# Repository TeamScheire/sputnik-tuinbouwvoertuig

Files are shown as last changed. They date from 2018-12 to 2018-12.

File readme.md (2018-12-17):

# Sputnik - de tuinbouwmachine

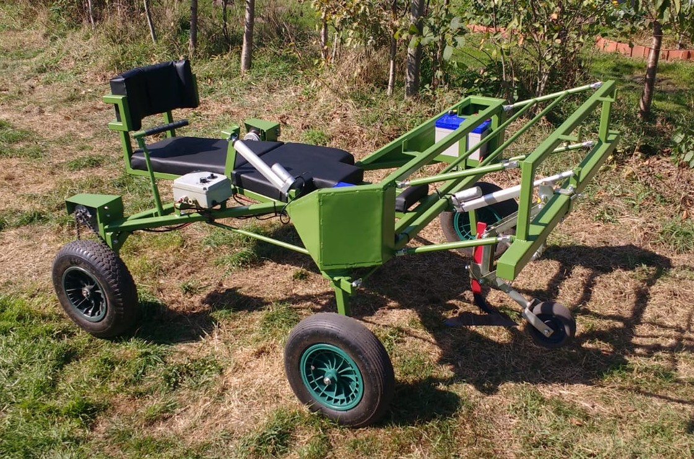
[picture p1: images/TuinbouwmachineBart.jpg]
sputnik


De sputnik is een tuinbouwmachine, speciaal en op maat gemaakt voor Bart, een persoon die een biologische deeltuin heeft, maar door een ski-ongeval in een rolstoel zit.

[Ronald Van Ham](https://github.com/RonaldVanHam) en [Elisa Van Coster](http://www.studiobasalt.be) werkten samen. Elisa ontwierp de machine en maakte het frame en besturing. Ronald deed de aansturing van de motoren.

In deze repo vind je:

- [Afbeeldingen](./images) met de afmetingen en details van de constructie
- [Broncode](./software) van de software
- [Ontwerpen](./designs) van de tandwielen en andere mechanicaonderdelen

## Frame

### Ontwerp

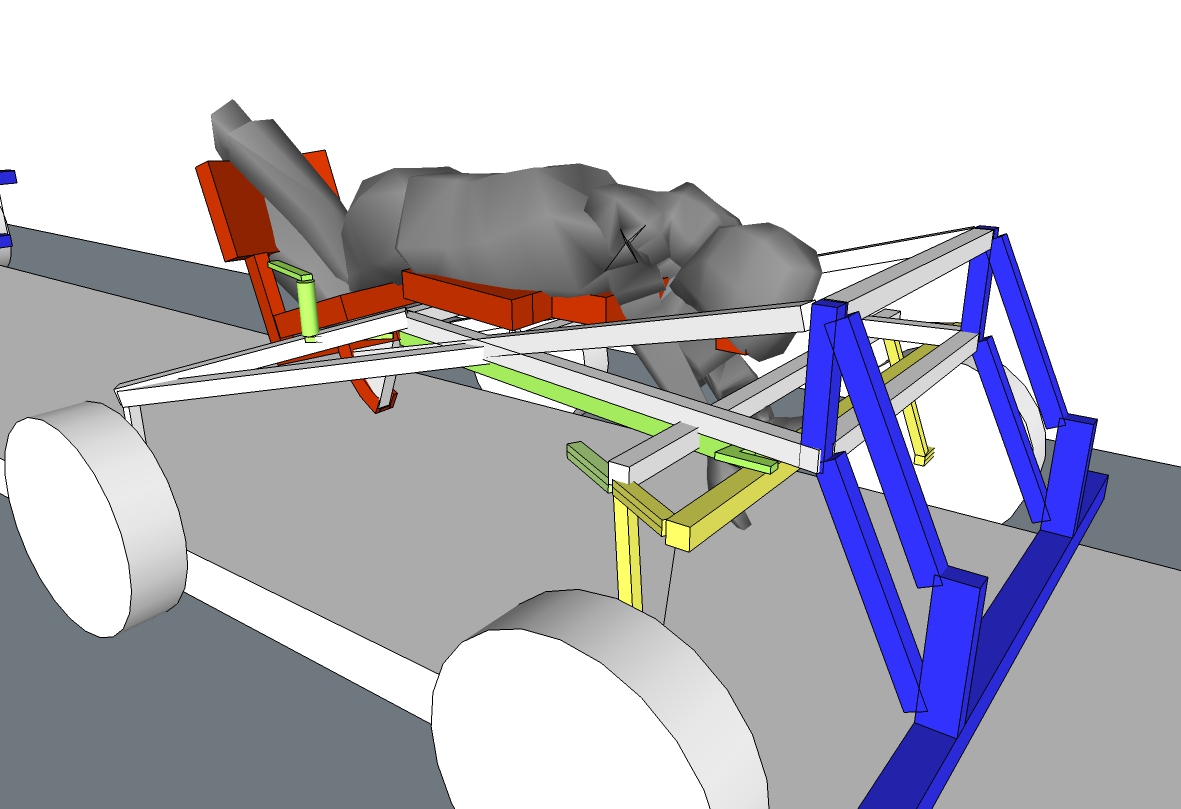
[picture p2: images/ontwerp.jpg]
ontwerp


- De gele delen zijn de onderdelen van het stuur.
- De rode delen zijn die van de stoel die in zit- en lighouding gezet kan worden.
- De blauwe delen zijn die van de werktuigenbalk die in hoogte versteld kan worden.

### Afmetingen

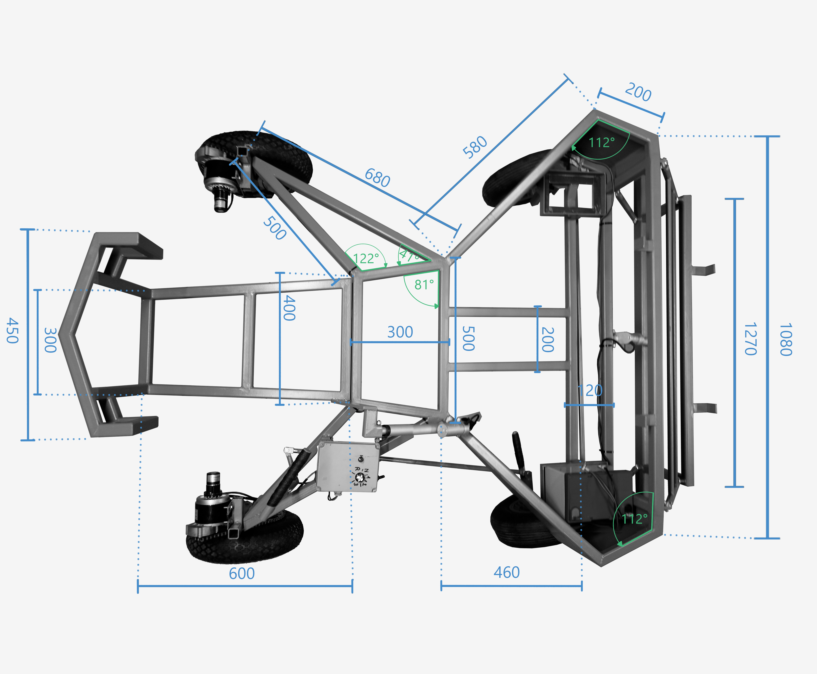
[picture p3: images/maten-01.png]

afmetingen-02

### Stuur

Het stuur zit op de voorstel wielen en is gebouwd volgens het [Ackermannprincipe](https://nl.wikipedia.org/wiki/Ackermann-principe)

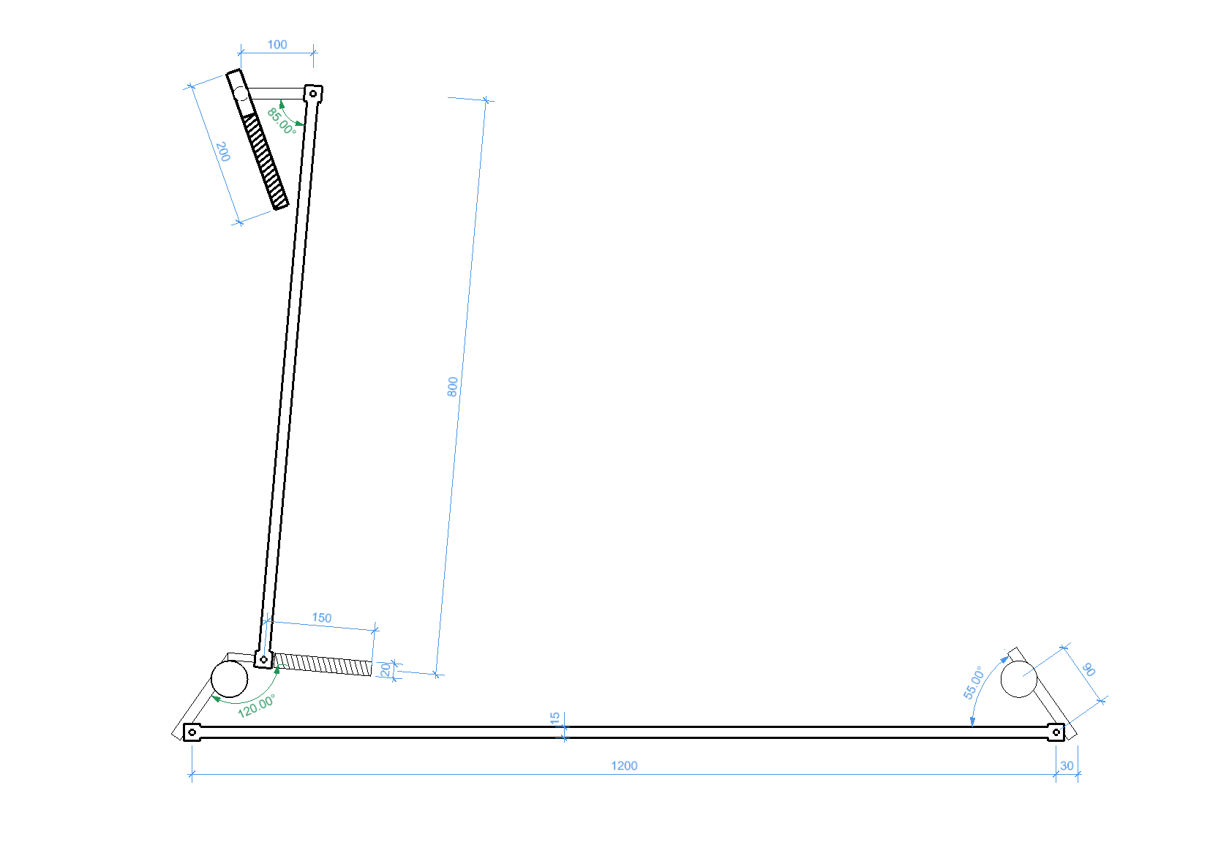
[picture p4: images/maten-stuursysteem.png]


### Details

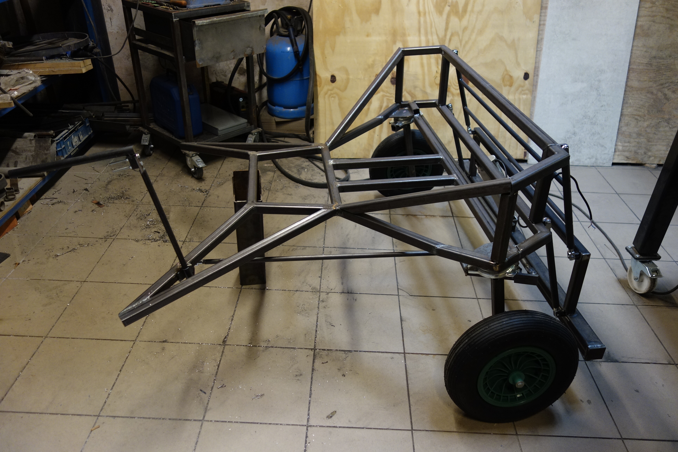
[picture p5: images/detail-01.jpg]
detail-01

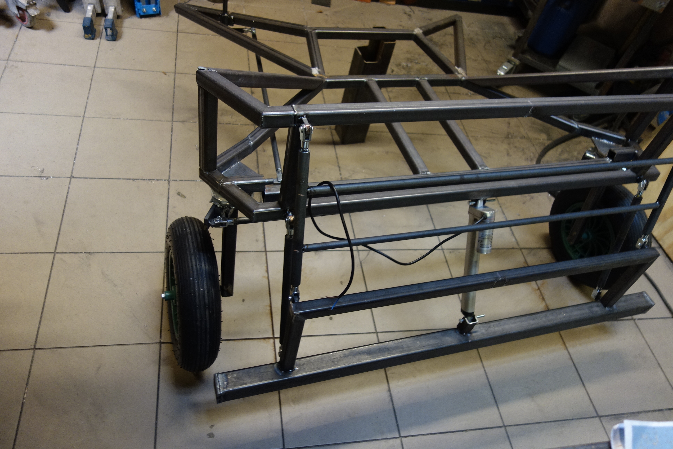
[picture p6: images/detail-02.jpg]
detail-02

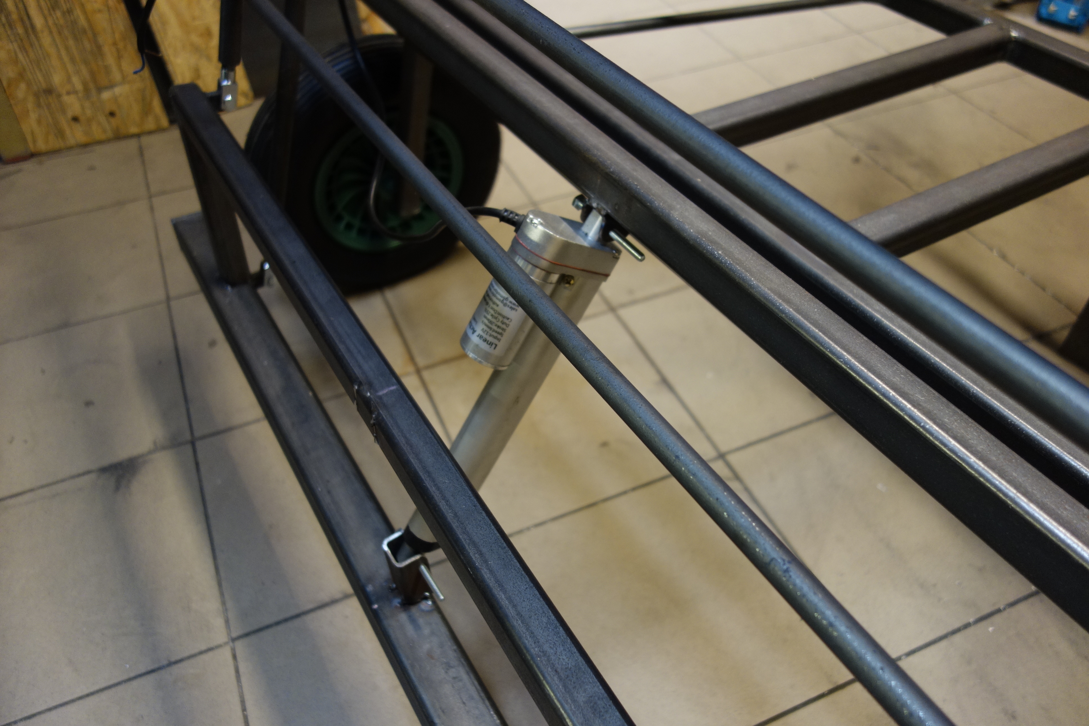
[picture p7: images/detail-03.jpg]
detail-03

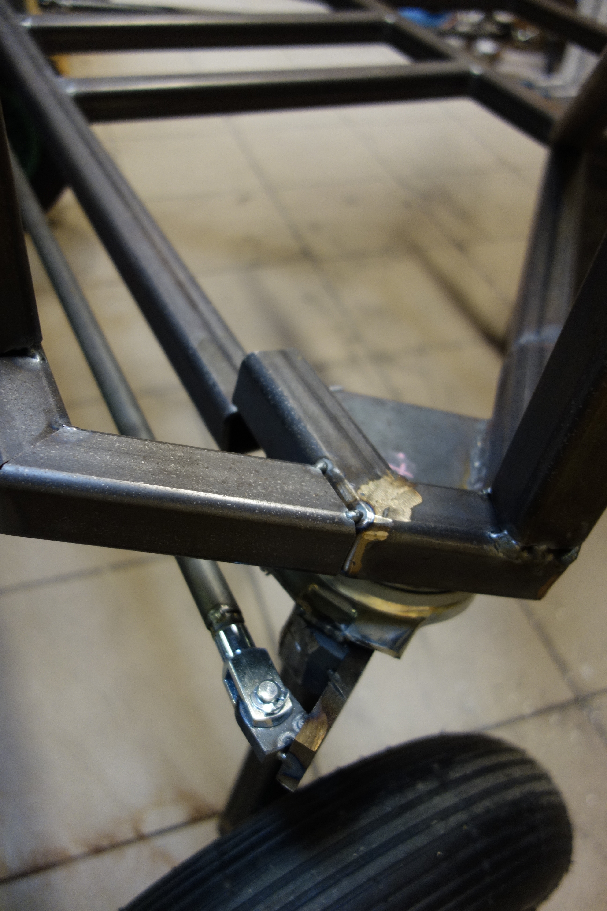
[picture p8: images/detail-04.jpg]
detail-04

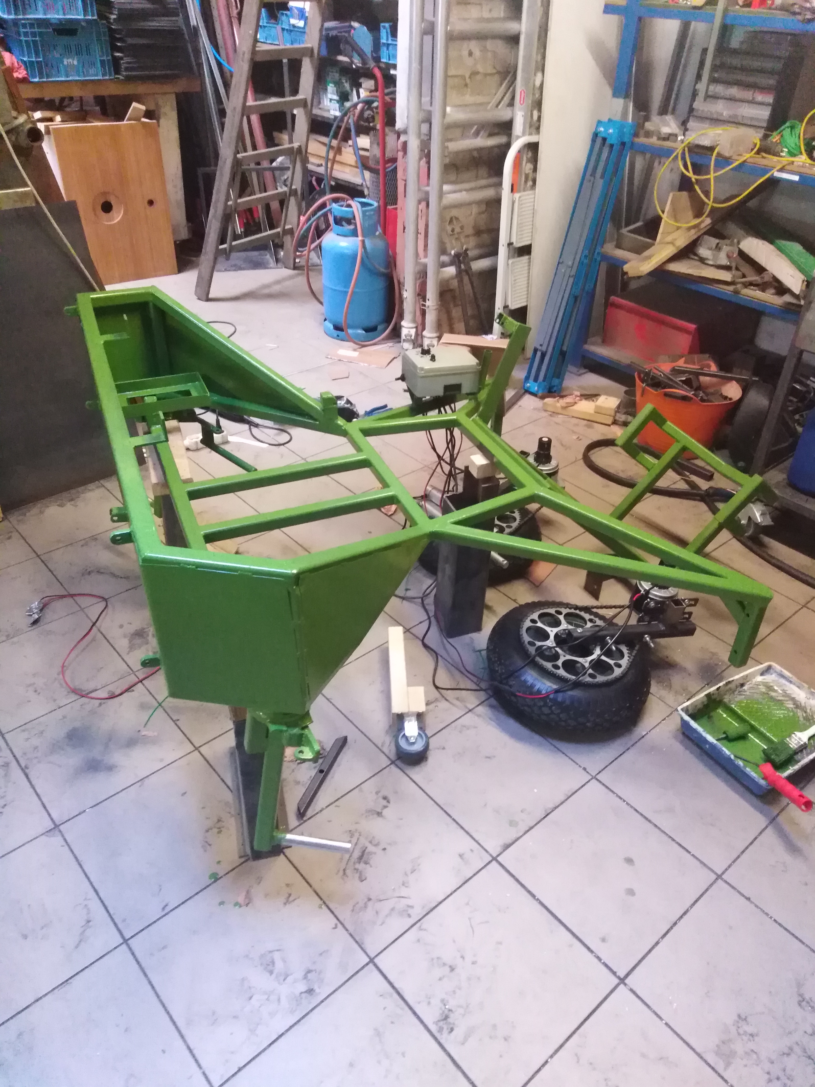
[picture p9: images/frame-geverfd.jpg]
geverfd
 	

## Motoren

Om over de gewassen te kunnen rijden met aandrijving zijn er in principe 2 opties: 

Eén motor gebruiken en de twee wielen verbinden met een as *of* twee keer op elk wiel een motor zetten. 

Bart wil kunnen zitten en liggen. Het zaaibed is bovendien hoger dan de zijpaden waar de wielen op rusten. Een as zou dus de gewassen raken. Vandaar is het snel duidelijk dat een motor op elk wiel de enige optie is.

### Aandrijving

De motoren die gebruikt worden voor de aandrijving, zijn te verkrijgen via [ali express](https://www.aliexpress.com/w/my1016z-12v.html) of [forandor](https://forandor.com/index.php?route=product/product&path=68&product_id=324)

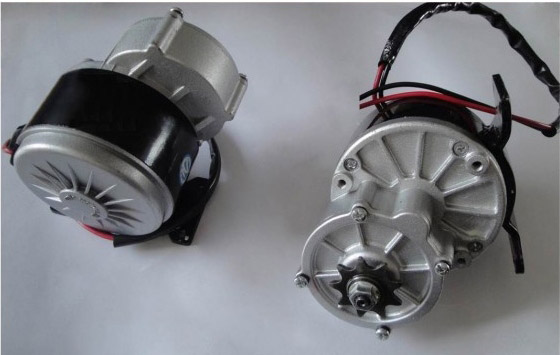
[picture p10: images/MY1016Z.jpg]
motor


### Lineaire actuatoren

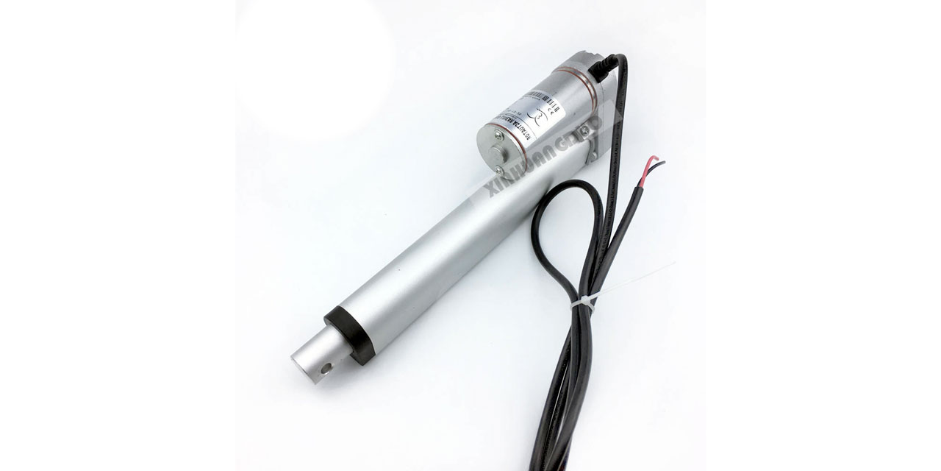
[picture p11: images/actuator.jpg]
Lineaire Actuatoren


De motoren die gebruikt zijn voor de beweging van de stoel en de werktuigenbalk zijn lineaire actuatoren. Deze zijn [hier te krijgen](https://www.aliexpress.com/item/Free-shipping-24v-150mm-6inch-stroke-mini-linear-actuator-electric-linear-actuator-thrust-900N-customized-stroke/1647892597.html) en hebben een stang die op en neer kan bewegen in een nauwkeurige positie.

## Aandrijving

De extra uitdaging is dat Bart zowel snel, maar vooral heel traag wil kunnen rijden. Normaal wordt hiervoor een motor met een mechanische versnellingsbak gebruikt, zoals bijvoorbeeld ook in een auto zit.

Maar er zijn twee motoren en twee versnellingsbakken zou het geheel vrij zwaar en de bediening moeilijk maken. Ze moeten immers altijd in dezelfde versnelling staan.

Een DC motor gebruiken heeft het nadeel dat als je de DC heel traag wil later draaien, je de spanning zo laag moet maken dat ook de stroom en het koppel te klein wordt om nuttig te zijn. Dus de motor gaat waarschijnlijk gewoon niet draaien. 

### Closed loop

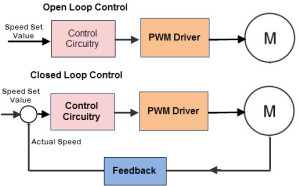
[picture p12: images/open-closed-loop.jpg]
closed loop


De DC motor wordt op een speciale manier aangestuurt, namelijk in 'closed loop'. Dat wil zeggen dat een snelheidsregelaar gebruikt wordt, geprogrammeerd in de [Arduino](./software/TuinbouwmachineBart/TuinbouwmachineBart.ino). 

We krijgen aan de ene kant een gevraagde snelheid via de potentiometer die Bart kan regelen. We gaan die in de controller vergelijken met de huidige snelheid die we meten via de optische encoder op de motor. We maken in de controller het verschil van deze twee snelheden. Dit noemen we de ‘fout’ (error) tussen wat we vragen en wat we meten. Deze fout gaan we gebruiken om de waarde van de PWM te bepalen. We gaan de fout met een bepaalde waarde vermenigvuldigen om de PWM waarde te krijgen, deze waarde noemen we de proportionele constante van onze regelaar. 

Dit gaat al redelijk werken, maar we merken op heel lage snelheden dat de motor toch gaat stilstaan, omdat de fout dan ook klein gaat zijn en de PWM waarde ook klein. Om dit op te lossen gaan we de fout 'integreren'. Dit wil zeggen dat we telkens de fout optellen en deze waarde vermenigvuldigen met een andere constante, de integrale constante van onze regelaar. Op deze manier gaat de PWM waarde verhogen als we langere tijd te traag draaien (of blijven stil staan). 

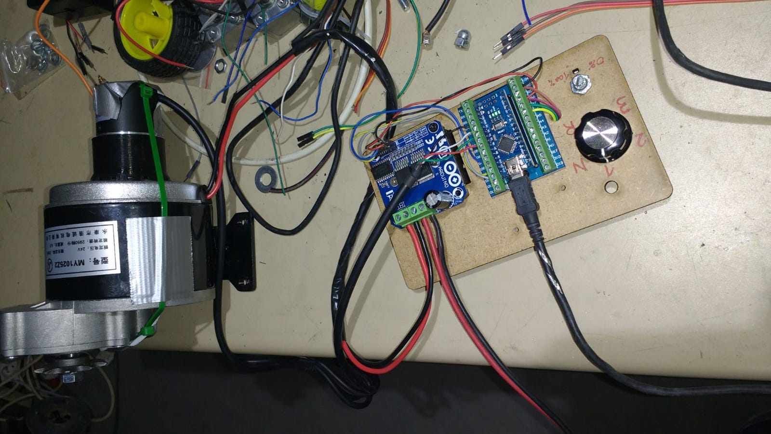
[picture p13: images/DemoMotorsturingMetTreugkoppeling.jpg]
demoopstelling


Nu komt het er op aan de 2 constanten van onze PI regelaar (proportioneel en integraal regelaar) juist in te stellen. Dit kan theoretisch aangepakt worden of we kunnen ze tunen ‘in the field’. Dit laatste is letterlijk te nemen, want Bart wil dat zijn machine traag door een veld kan rijden. Dit wil zeggen dat de weerstand kan veranderen naargelang er meer grond voor de wielen ligt of hij aan het rijden of schoffelen is. Dit theoretisch benaderen is moeilijk, want we hebben geen waarden van de weerstand die Bart gaat ondervinden op zijn veld. 

In dit geval hebben we bij deze waarden wel wat marge omdat gaat het om een tuinbouwmachine, waarbij de snelheid moet geregeld kunnen worden, maar ook niet super precies hoeft te zijn. Dus we gaan de waarden in ons atelier instellen en nadien aanpassen op het veld indien nodig.

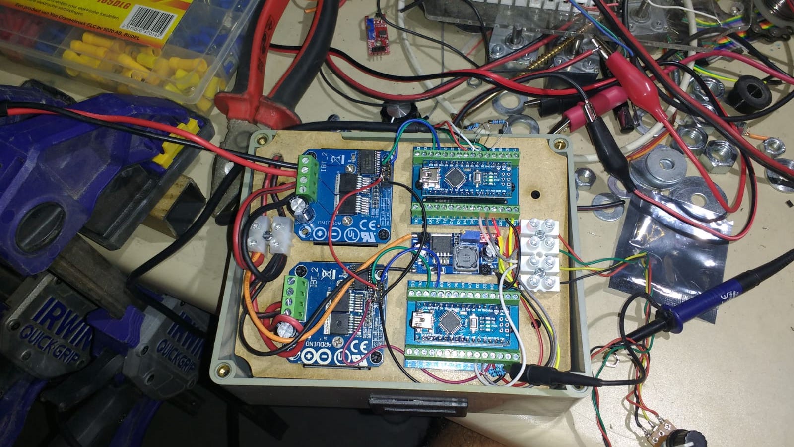
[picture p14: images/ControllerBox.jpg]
controllerbox


### De instelling van de gevraagde snelheid.

Omdat een potentiometer in de lage snelheden moeilijk in te stellen is, werken we met softwarematige versnellingen. We hebben een 2de knop geplaatst waarmee Bart kan kiezen tussen 1 versnelling achteruit, neutraal en 3 versnellingen vooruit. Dus de software gaat bij de achteruitstand van de knop, de richting van de motor omdraaien en de gevraagde snelheid beperken. Achteruit moet Bart immers niet zo snel kunnen rijden. Vooruit hebben we de snelheid in 3 stappen ingesteld. In 3de versnelling kunnen we de motor op volle snelheid aansturen, in 2de ongeveer zo snel als achteruit, en in 1ste heel traag. Dus de volledige toer van de potentiometer wordt herschaald naar een beperkt deel van de snelheid. Zo kan Bart ook op lage snelheden zijn gevraagde snelheid vrij precies instellen.

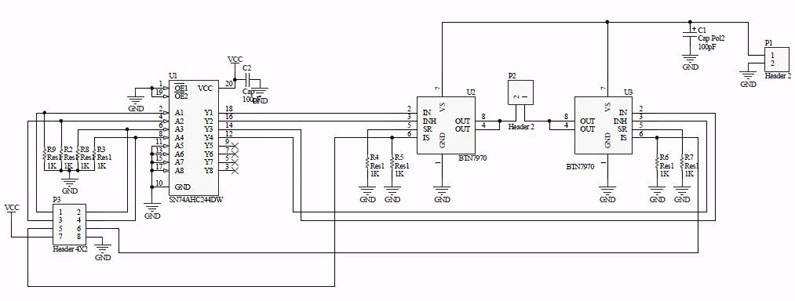
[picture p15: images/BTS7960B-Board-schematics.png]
schematics


We hebben dus 2 snelheidsgestuurde motoren. Gevolg is dat de 2 wielen ook quasi even snel gaan draaien. Dit komt overeen met een starre achteras, dus zonder differentieel. Een differentieel bij een auto is een mechanisme met tandwielen dat toelaat dat de 2 wielen met een verschillende snelheid draaien. Dit is nodig als je een bocht neemt met een auto. Door onze 2 motoren in snelheid te sturen gaan de wielen in een  bocht even snel draaien en dus op de grond slippen. Om dit te vermijden gaan we in 3de versnelling en in achteruit de controle open loop doen, dus geen snelheidsterugkoppeling, en dus een soort softwarematige of elektrische differentieel. In 1ste en 2de gaat de closed loop werken, omdat we dan normaal geen grote bochten gaan maken en we daar die closed loop controle nodig hebben om de motoren traag te kunnen laten draaien. Hier rijden we dan alsof we een ‘sper-differentieel’ of starre achteras hebben.

### Andere types motoren

We hebben geopteerd voor een DC motor omdat dit voor de meeste makers gemakkelijker is in gebruik. Er bestaan ook brushless DC motoren (zonder koolborstels en met elektronische commutatie). Deze kunnen ook open loop en closed loop gebruikt worden. Om de positie en snelheid te meten, gebruiken deze meestal Hall sensoren. Deze dienen om de elektronische commutatie goed te kunnen aansturen maar zorgen ook meteen voor een feedback op de snelheid. Dit is te vergelijken met de encoder en closed loop DC motor die wij gebouwd hebben, alleen is de driver wat complexer in gebruik en ook complexer om uit te leggen tegenover de H-Brug bij de gewone DC motor.

## Afgewerkt

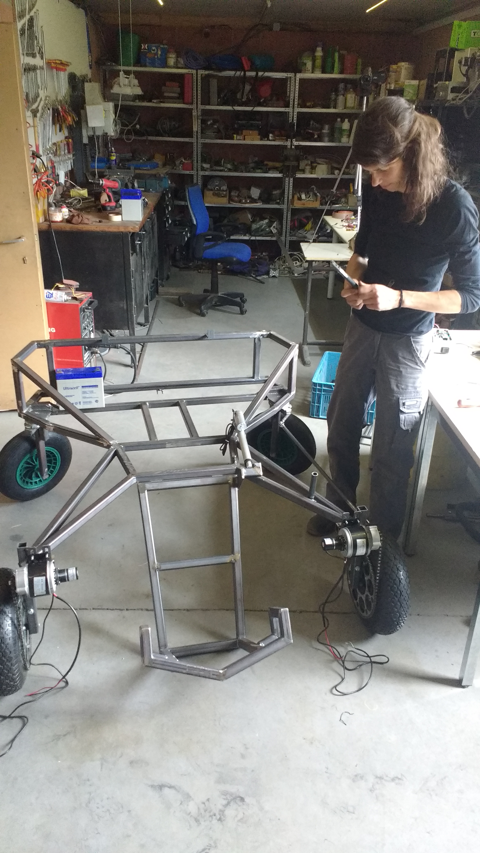
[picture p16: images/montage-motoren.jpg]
motoren

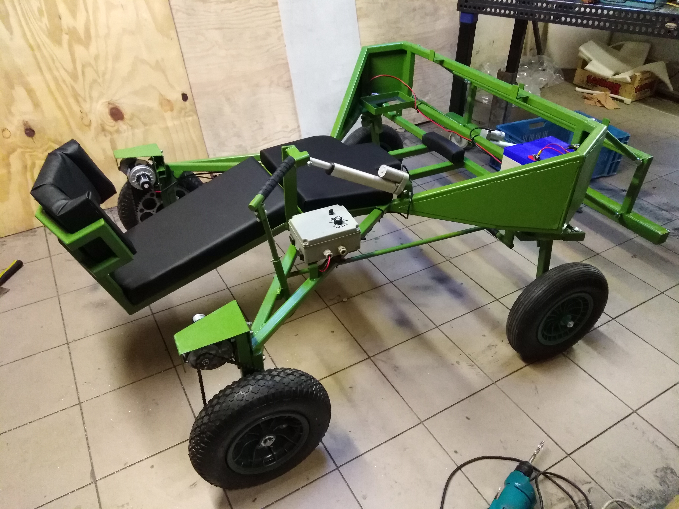
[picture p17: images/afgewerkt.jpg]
afgewerkt


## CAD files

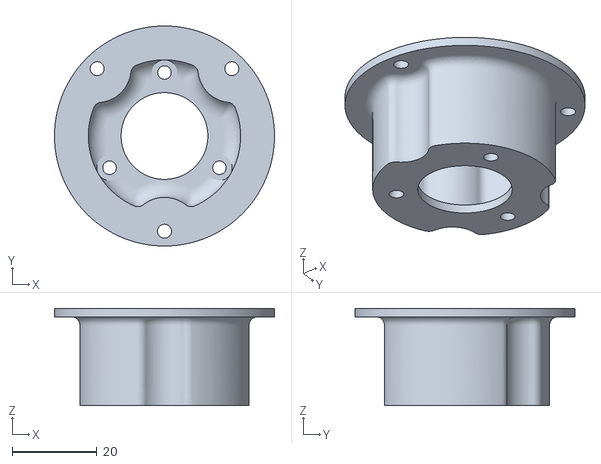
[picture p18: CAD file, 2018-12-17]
designs/EncoderHouder Potje om te schroeven.stl
52.0 x 52.0 x 23.0

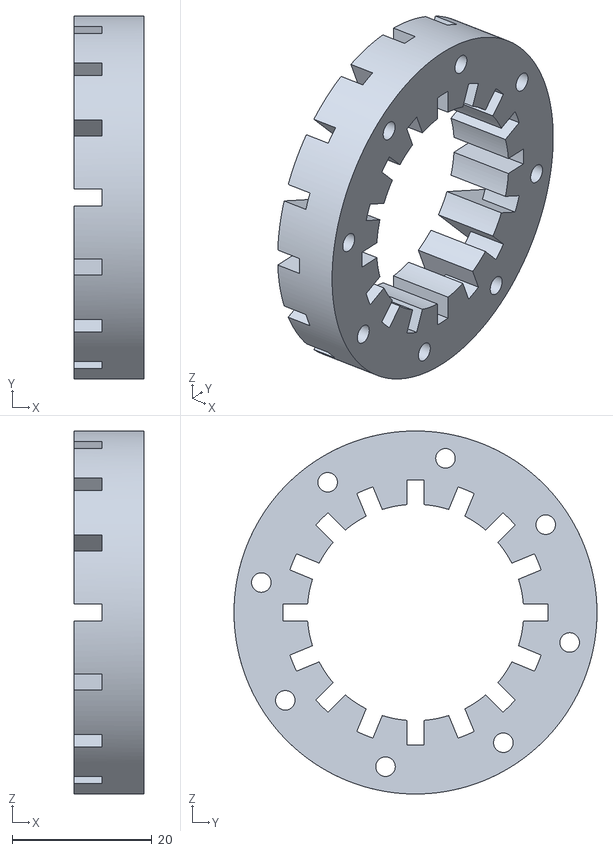
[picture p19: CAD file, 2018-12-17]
designs/EncoderHouder Lijmstuk op MY1016.stl
10.0 x 52.0 x 52.0

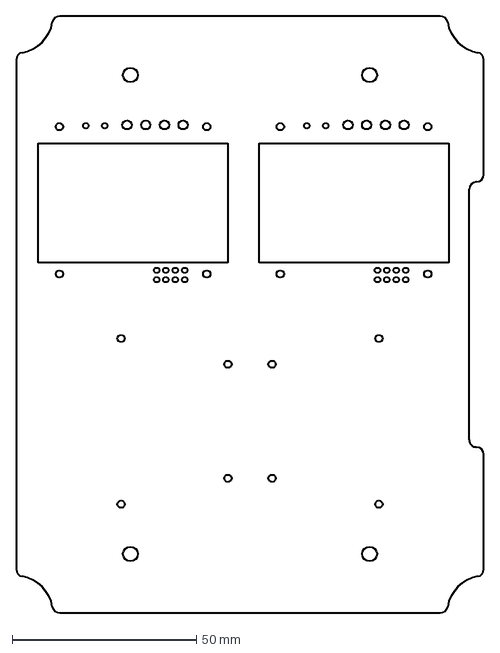
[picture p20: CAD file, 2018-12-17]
designs/BaseplateMotor02.dxf
127.0 x 162.0 mm

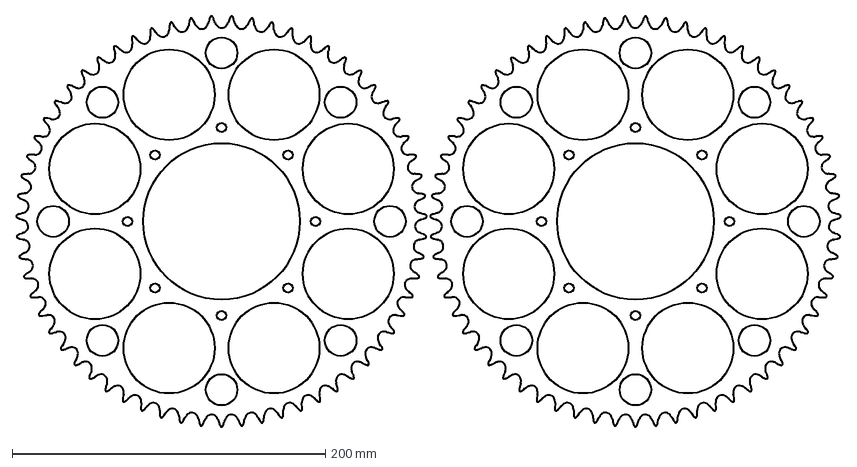
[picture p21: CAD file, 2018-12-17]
designs/2xTandwiel63tanden Lasercut.dxf
526.2 x 261.9 mm

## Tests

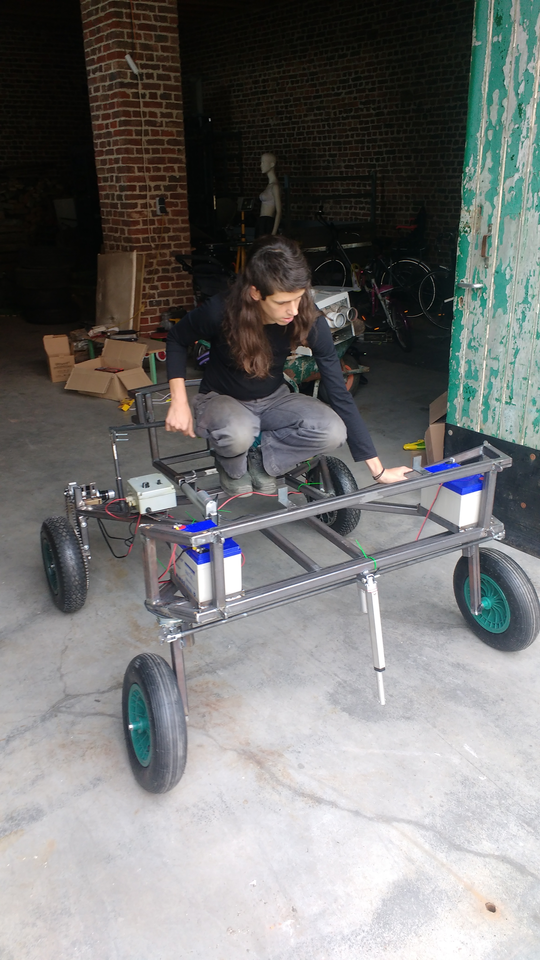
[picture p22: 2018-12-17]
images/eerste-testrit.jpg

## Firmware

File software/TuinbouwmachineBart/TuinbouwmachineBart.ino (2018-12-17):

/* Arduino Code voor de beide arduino nano in de tuinbouwmachine van Bart. Deze code kan voor andere closed loop DC motoren gebruikt worden
 * pin 2 en 3 optische encoder op de motor
 * pin4 +5V voor de encoder
 * pin8 +5V voor de H-brug logica 
 * pin 13 led pin en test pin
 * pin 9 en pin 10: PWM uitgangen naar de H-brug
 
 */

int Control = 0;            // Interne waarde van de potentiometer voor de snelheid
int ControlPower = 0;       // 
int ExtraPower = 0;
int Gear = 0;               // 1 tot 5 voor de versnellingen: 0 = achteruit, 1 = neutraal, 2 = 1ste, 3 = 2de, 4 = 3de vooruit

int PWMout1 = 0;        // Interne waarde voor PWM1 (analog out)
int PWMout2 = 0;        // Interne waarde voor PWM2 (analog out)

#define EncPinA  2  // interrupt pin
#define EncPinB  3  // een andere pin, zou ook interrupt kunnen geven
volatile int EncPos = 512;

void setup() {

  Serial.begin(115200);                                         // Start de seriele communicatie
  pinMode(EncPinA, INPUT);   digitalWrite(EncPinA, HIGH);       // encoder pinnen input en pull-up weerstand
  pinMode(EncPinB, INPUT);   digitalWrite(EncPinB, HIGH);       // encoder pinnen input en pull-up weerstand

  pinMode(4, OUTPUT);   digitalWrite(4, HIGH);                  // 5V voor de Encoder
  pinMode(8, OUTPUT);   digitalWrite(8, HIGH);                  // 5V voor de H-Bridge
  pinMode(13, OUTPUT);  digitalWrite(13, LOW);                  // Test LED 
  
  pinMode(9, OUTPUT);                                           // PWM Pin 1
  pinMode(10, OUTPUT);                                          // PWM Pin 2
  ControlPower = 127;

  //Setup Timer2 overflow to 16ms as watchdog timer - Zie internet od atmega datasheet
  TCCR2B = 0x00;        //Disbale Timer2 while we set it up
  TCNT2  = 0;           //Reset Timer Count to 0 out of 255
  TIFR2  = 0x00;        //Timer2 INT Flag Reg: Clear Timer Overflow Flag
  TIMSK2 = 0x01;        //Timer2 INT Reg: Timer2 Overflow Interrupt Enable
  TCCR2A = 0x00;        //Timer2 Control Reg A: Wave Gen Mode normal
  TCCR2B = 0x07;        //Timer2 Control Reg B: Timer Prescaler set to 1024

  interrupts();  // zet de interrupts hoofdschakelaar aan
}

void loop() {
  TCNT2 = 0;  // reset timer 2 = onze eigen watchdogtimer
  digitalWrite(13, HIGH);   // Om te tijd van 1 controle lus te kunnen checken met een oscilloscoop
  digitalWrite(13, LOW);    // Genereren we hier een puls

  Control = analogRead(A7);               // Lees de gewenste snelheid uit, potentiometer  van Bart
  //           if (Control < 10) { delay(10);}       // **** Watchdog Timer (timer2) Test code
  
  Gear = map(analogRead(A6),0,1024,0,5);   // verdeel de versnelingspotentiometer in 5 levels
  switch (Gear) {

     case 0:
       Serial.print("R ");     // Achteruit     -  geen encoder feedback - differentieel 
       Control = map(analogRead(A7),0,1023,256,512);
       break;
     case 1:
       Serial.print("N ");     // Neutraal - geen aansturing - differentieel 
       Control = 512;
       break; 
     case 2:
       Serial.print("1 ");      //  1st versnelling -  met ecoder feedback - starre achteras
       Control = map(analogRead(A7),0,1023,512+64,512);
       break;
     case 3:
       Serial.print("2 ");     //  2de versnelling -  met encoder feedback - starre achteras
       Control = map(analogRead(A7),0,1023,512+128,512); 
       break;   
     case 4:
       Serial.print("3 ");     //  3de versnelling - zonder encoder feedback- differentieel 
       Control = map(analogRead(A7),0,1023,512+512,512); 
       break;
    }
     

  PWMout1 = 1;      // We gaan er van uit dat de motor moet stilstaan, indien niet wordt dit in de volgende lijnen aangepast  
  PWMout2 = 1;  


  // Volgende lijnen: zet de PWM uitgangen afhankelijk van gevraagde snelheid en keuze van de versnelling en richting
  if (Gear == 0) { PWMout1 = 1; PWMout2 = map(Control,512,256,0,128); }  // Geen encoder feedback  
  if (Gear == 4) { PWMout1 = map(Control,512,1024,0,255); PWMout2 = 1; } // Geen encoder feedback
  if ((Gear == 2) or (Gear == 3)) {          
    ControlPower = (Control + ExtraPower) / 4 ;                          // met encoder feedback
    if (ControlPower <   0) {ControlPower =   0;}
    if (ControlPower > 255) {ControlPower = 255;}
    if (ControlPower > 127) {PWMout1 = map(ControlPower,128,255,5,255); PWMout2 = 1; }  
    if (ControlPower < 127) {PWMout2 = map(ControlPower,126,  0,5,255); PWMout1 = 1; }
    }
  // In neutraal laten we ze beide op 1 staan

  analogWrite(9, PWMout1);  // PWM1 effectief naar de H-Brug sturen
  analogWrite(10, PWMout2); // PWM2 effectief naar de H-Brug sturen 
  
  EncPos = 512; // 512 = nul, higher is one direction, lower than 512 is the other direction
  attachInterrupt(0, doEncoder0, CHANGE);  // encoder pin on interrupt 0 - pin 2
  delay(10);                               // Tel pulsen gedurende 10 ms  
  detachInterrupt(0);                      // Zet interrupt terug af


  ExtraPower = ExtraPower + 1 * (Control - EncPos);
  if (ExtraPower < -250) {ExtraPower = -250;}
  if (ExtraPower >  250) {ExtraPower =  250;}

  /*  // Om te debuggen kan je data doorsturen naar de PC
  Serial.print(EncPos);
  Serial.print("\t  ");
  Serial.print(Control);
  Serial.print("\t  ");
  Serial.print(ExtraPower );
  
  Serial.print("\t 1L ");
  Serial.print(PWMout1 );
  Serial.print("\t 2L ");
  Serial.print(PWMout2 );
  Serial.println( );
  */ 
}
// Einde Hoofdprogramma

// Interrupt Service Routine voor de Encoder uit te lezen en om te zetten naar snelheid met 512 als stilstand
void doEncoder0() {
  if (digitalRead(EncPinA) == digitalRead(EncPinB)) {
    if (EncPos < 1024)  EncPos=EncPos+1;      // We zorgen dat de positie steeds tussen 0 en 1024 blijft
  } else {
    if (EncPos > 0)    EncPos=EncPos-1;       // We zorgen dat de positie steeds tussen 0 en 1024 blijft
  }
}

// Volgende code is voor onze eigen watchdog functie. Als de timer overflowed (dan loopt het programma niet zoals verwacht) resetten we de Arduino
void(* resetFunc) (void) = 0; //declare reset function @ address 0

ISR(TIMER2_OVF_vect) { // Timer2 = Watchdog interrupt
  TIFR2 = 0x00;        // reset timer 2 = onze eigen watchdogtimer
  Serial.print("**");
  resetFunc();         // call reset, herstart de Arduino
}
